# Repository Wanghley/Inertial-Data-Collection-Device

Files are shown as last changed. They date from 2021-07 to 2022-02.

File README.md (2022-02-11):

Inertial Data Collection Device<br>
      

>  printed circuit board and code for collecting inertial data to research purposes of movements.

## About
Hardware developed to collect inertial data from human's hands (i.e. Accelerometer, Giroscope) and temperature in order to provide an open source hardware for research related to the analysis of human movements for many purposes.<br>
This project was tested and focused on the diagnosis and prognosis of neuromotor diseases - mostly Parkinson's Disease as part of the project of scientific research [**"Visualization Strategies to Online Big Data applied in individualized medicine"**](https://github.com/Wanghley/PIBIC-Strategies-Data-Visualization-Medicine).

## Requirements
| Dependency | Platform | Description |
| :--------- | -------- | :---------- |
| [arduino_2012](https://github.com/Wanghley/Inertial-Data-Collection-Device/blob/main/lib/arduino_2012.lbr) | eagle lib | arduino schematic and layout to **Eagle** project |
| [con-headers-jp](https://github.com/Wanghley/Inertial-Data-Collection-Device/blob/main/lib/con-headers-jp.lbr) | eagle lib | schematic and layout of female pin bars to **Eagle** project |
| [DIY modules](https://github.com/Wanghley/Inertial-Data-Collection-Device/blob/main/lib/diy-modules.lbr) | eagle lib | bluetooth adaptor fotoprint and symbol to **Eagle** project |
| [KRE](https://github.com/Wanghley/Inertial-Data-Collection-Device/blob/main/lib/kre.lbr) | eagle lib | borne connector fotoprint and symbol to **Eagle** project |
| [pinhead](https://github.com/Wanghley/Inertial-Data-Collection-Device/blob/main/lib/pinhead.lbr) | eagle lib | added in the **Eagle** project for auxiliary view of pin bars |
| [TimerOne 1.1.0](https://github.com/Wanghley/Inertial-Data-Collection-Device/blob/main/lib/TimerOne-1.1.0.zip) | arduino lib | allow running a periodic interrupt function based in finer PWM control |
| [MPU6050 0.2.1](https://github.com/Wanghley/Inertial-Data-Collection-Device/blob/main/lib/MPU6050-0.2.1.zip) | arduino lib | allow MPU6050 easy control and manipulation |
| [Wire](https://www.arduino.cc/en/reference/wire) | arduino lib | allow communication over I2C protocol |
| [SoftwareSerial](https://www.arduino.cc/en/Reference/softwareSerial) | arduino lib | allow serial communication on other digital pins of the Arduino |

## Bill of Materials
| # | Designator | Qty | Description | Obs |
| - | :--------- | --- | :---------- | :---------- | 
| 1 | R1, R2 | 2 | Resistor 220R 5% (1/4W) | Used for digital protection of bluetooth module RX |
| 2 | HC-05 | 1 | HC-05 Bluetooth Module | Module of Low supply consumption for prototype communication |
| 3 | PUSH | 2 | Push Button Long Head | Push button for hardware control and operation  |
| 4 | ON/OFF | 1 | 255sb sliding switch | Sliding switch to control energy supply of the prototype |
| 5 | LED1 | 1 | COM-09590 | 2.25 V Red LED 5mm Cylindrical indicates the hardware is ready for collection |
| 6 | LED2 | 1 | COM-09590 | 2.25 V green LED 5mm Cylindrical indicates the hardware operation mode and collection in process |
| 6 | Arduino Nano | Arduino Nano | | mother board and controller |
| 7 | KRE-2P | 1 | Borne Connector | Connector to the batery |
| 8 | BATTERY CHARGER | 1 | TP4056 | Power supply adn voltage regulator to the batery |
| 9 | RGB_LED | 1 | LED RBG 5MM | RGB LED 5mm Cylindrical indicates the mode of operation of the device |

## Development
In order to run and contribute to the PCB development you must have **Eagle**  installed in your computer and then use the .sch to work on the circuit itself and the .brd to work in the layout design.

Now, for the development under de code of hardware control you must have Arduino IDE or similar to work on the .ino code plus all the libraries mentioned above on the field [Requirements](#Requirements).

## Versioning
We use [SemVer 2.0.0](https://semver.org/spec/v2.0.0.html) for versioning. For the versions available, see the [tags on this repository](https://github.com/Wanghley/Inertial-Data-Collection-Device/tags).

## Authors
<table>
  <tr>
    <td align="center">
      <a href="https://github.com/wanghley">
        Foto do Wanghley no GitHub<br>
        <sub>
          <b>Wanghley Soares Martins</b>
        </sub>
      </a>
      <p>Researcher</p>
    </td>
    <td align="center">
      <a href="https://github.com/oliveirafhm">
        Foto do prof. Fábio no GitHub<br>
        <sub>
          <b>Fábio Henrique M Oliveira</b>
        </sub>
      </a>
      <p>Research Advisor</p>
    </td>
  </tr>
</table>

See also the list of [contributors](https://github.com/Wanghley/PIBIC-Strategies-Data-Visualization-Medicine/contributors) who participated in this project.

## License
This project is licensed under the CC BY-NC-SA 4.0 License - see the [LICENSE.md](LICENSE.md) file for details

## Acknowledge
*   Remember, the project is free for you to use, manipulate, and change. However, I am just asking you to mention us in any copy, modification as the root of your development. We would also appreciate you citating us in any paper you publish using any knowledge we had developed here.
*   I would advice you to try out the hardware with an analysis of the result data.
*   If you want an easier software for hardware control, check out the [CONTROL SOFTWARE](https://github.com/Wanghley/PIBIC-Strategies-Data-Visualization-Medicine)

## Gallery
General view of the projected PCB. For more images go to [images/](https://github.com/Wanghley/Inertial-Data-Collection-Device/tree/main/images) and if you still want to see more you can see 3D views on [view/](https://github.com/Wanghley/Inertial-Data-Collection-Device/tree/main/view)

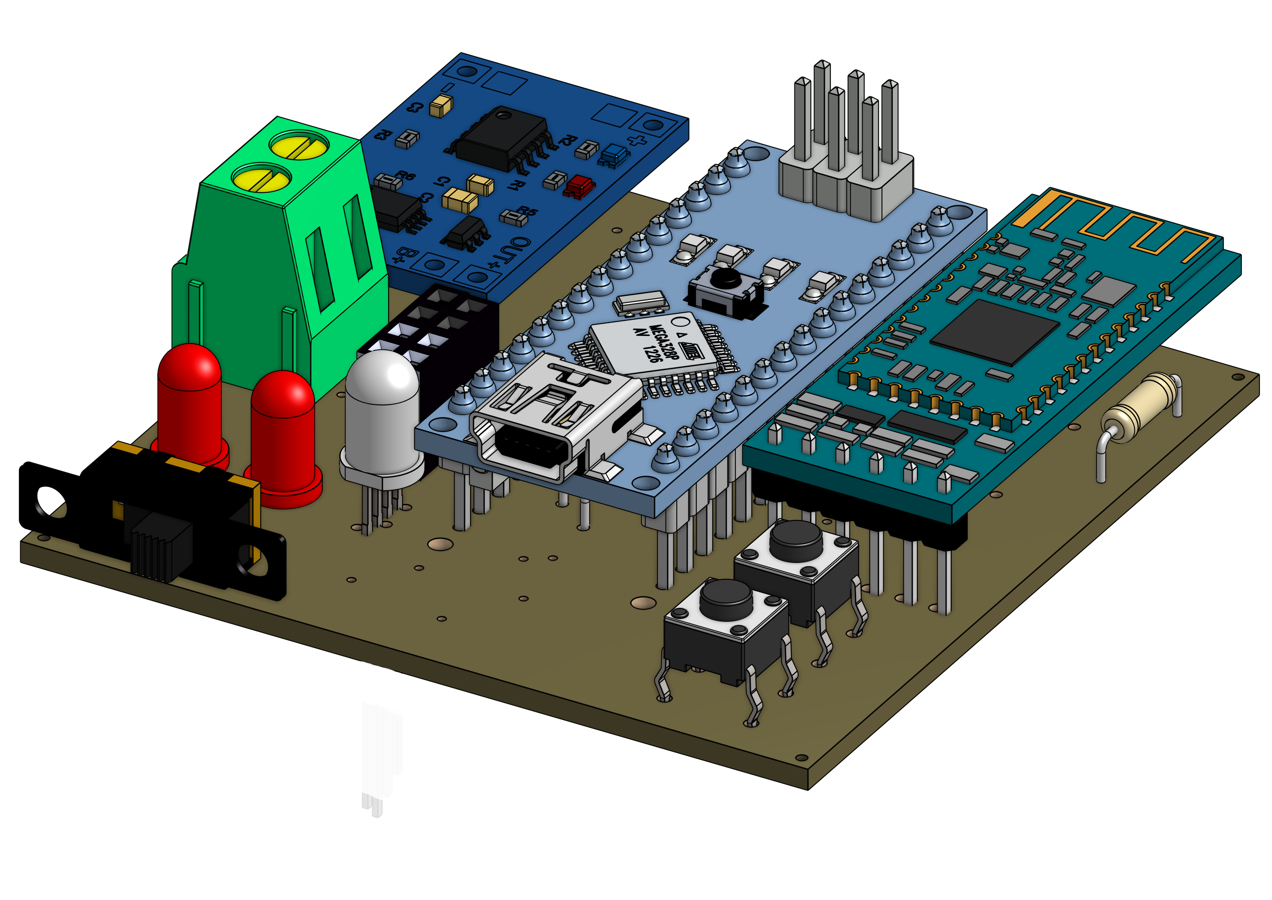
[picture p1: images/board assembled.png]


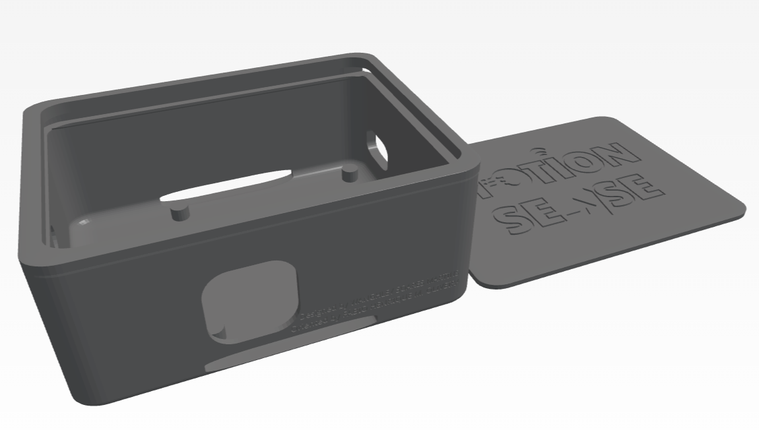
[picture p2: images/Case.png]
Case 3D view


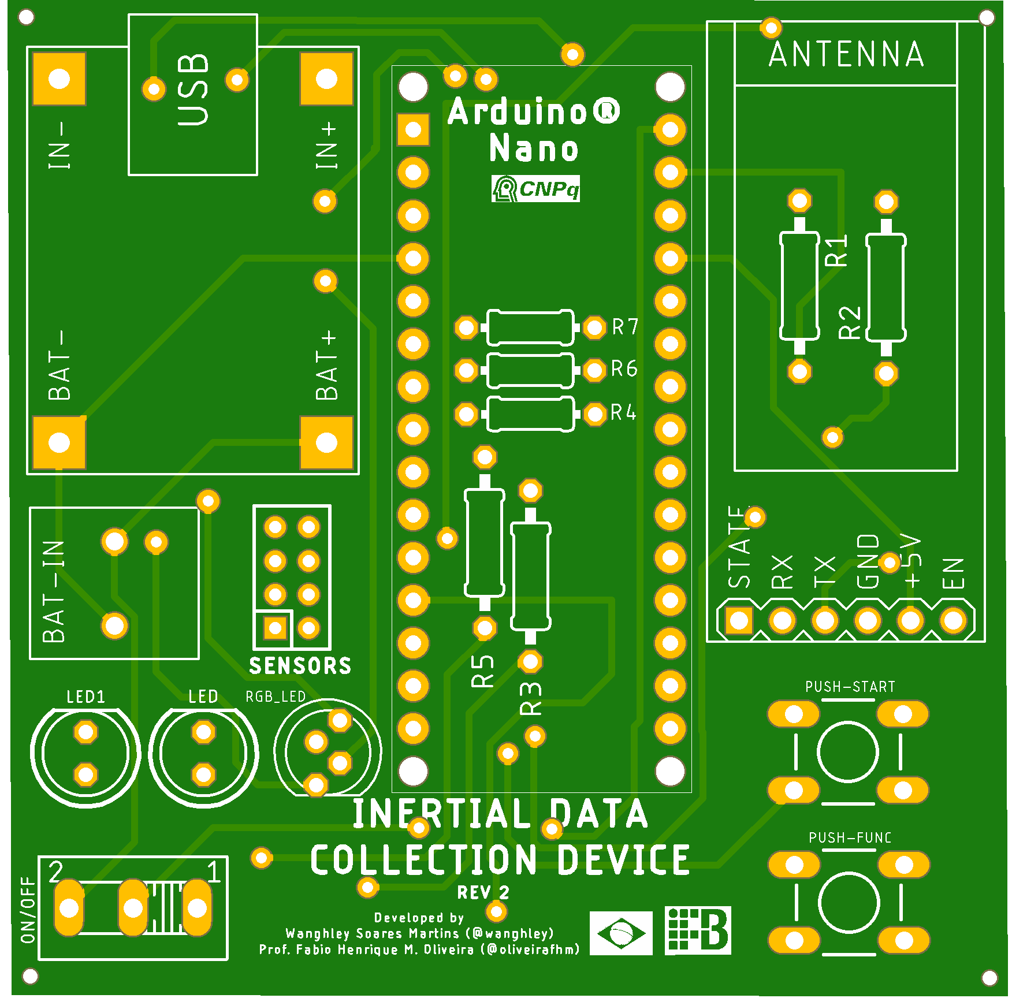
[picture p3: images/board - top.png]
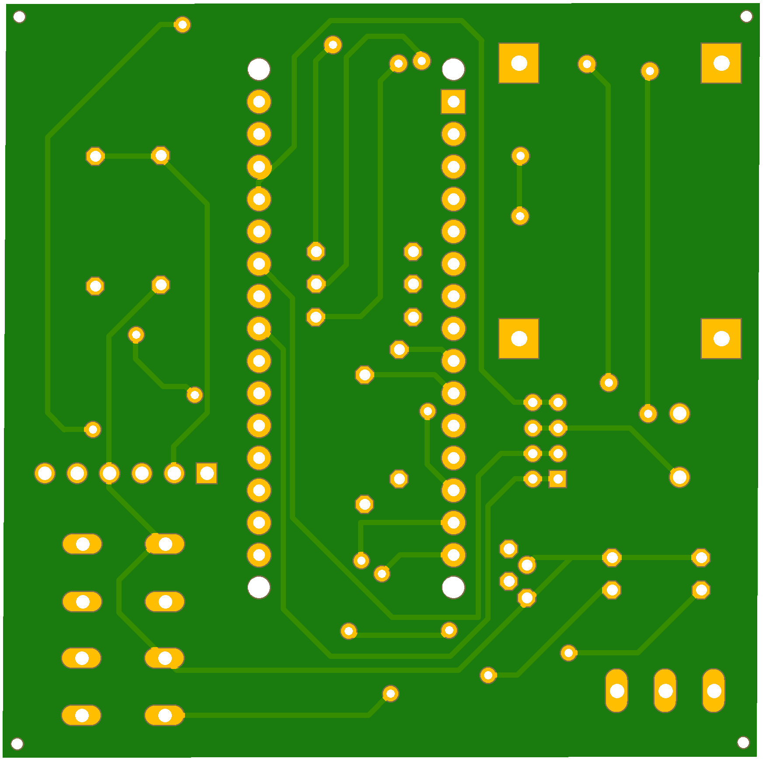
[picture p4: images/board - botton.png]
|  | |
|-|-|

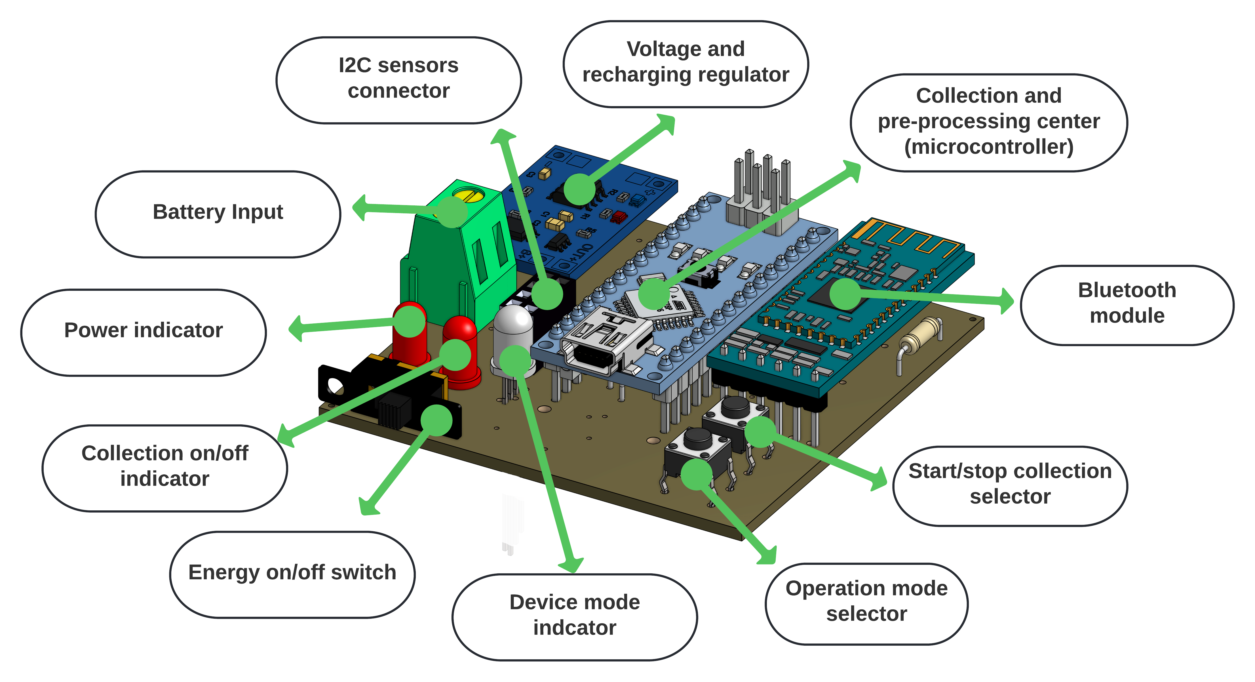
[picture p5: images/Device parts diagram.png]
Device parts diagram


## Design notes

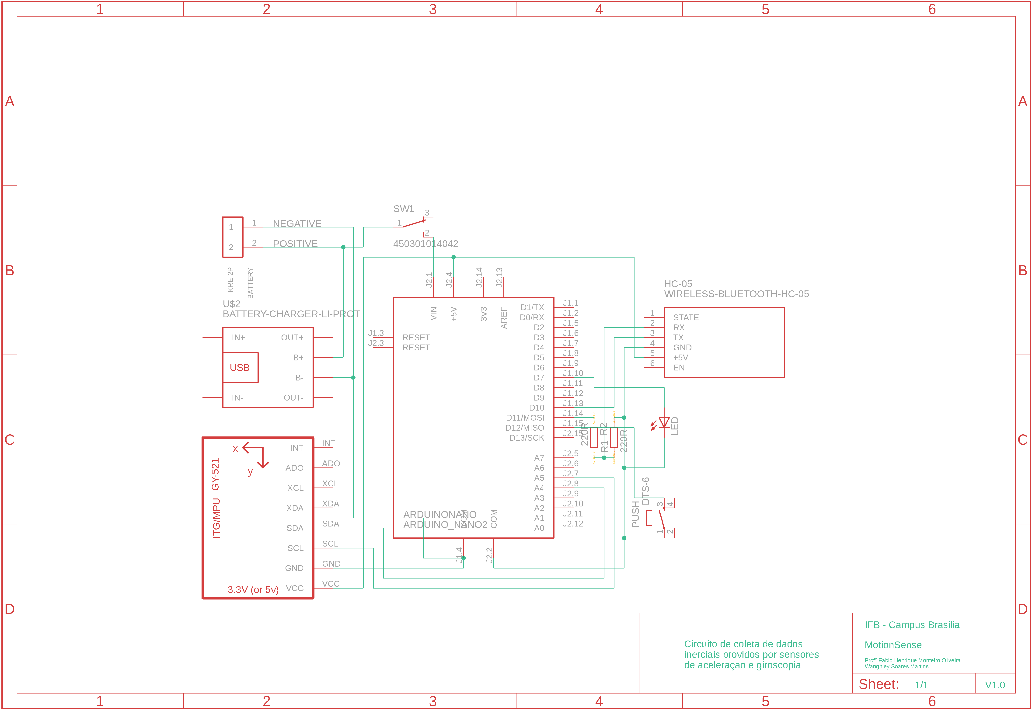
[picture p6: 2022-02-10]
images/sch.png

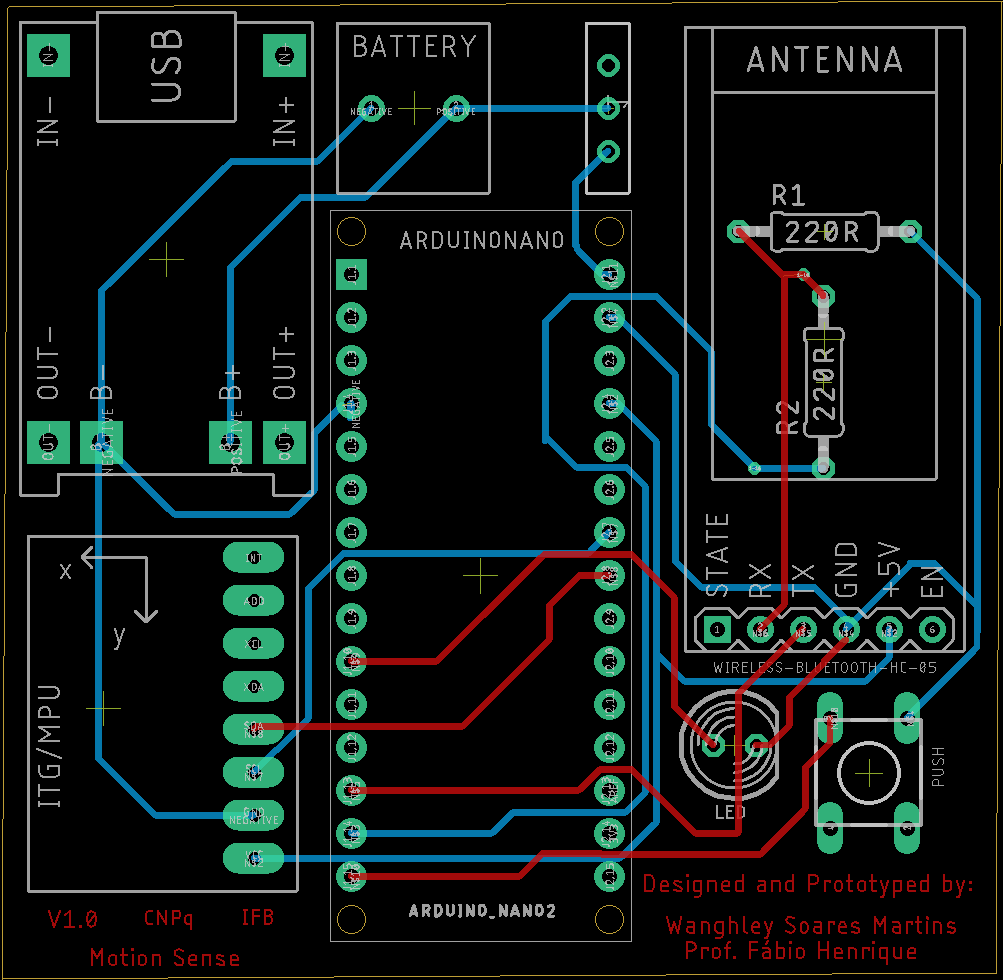
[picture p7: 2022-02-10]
images/pcb.png

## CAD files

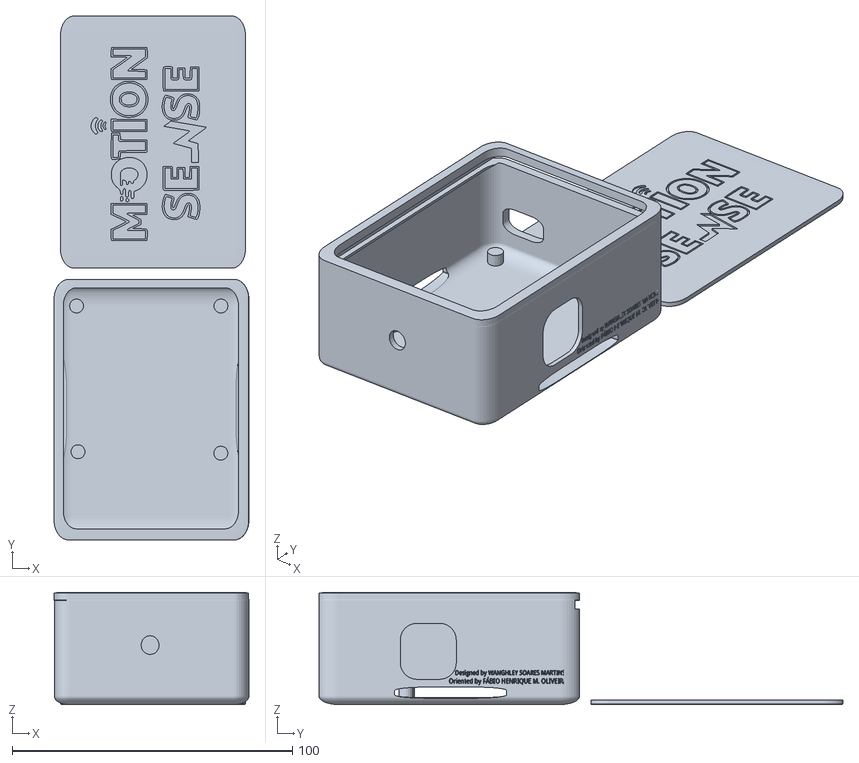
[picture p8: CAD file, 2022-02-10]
component/Complete Motion Sense Box.stl
69.5 x 187.0 x 40.0

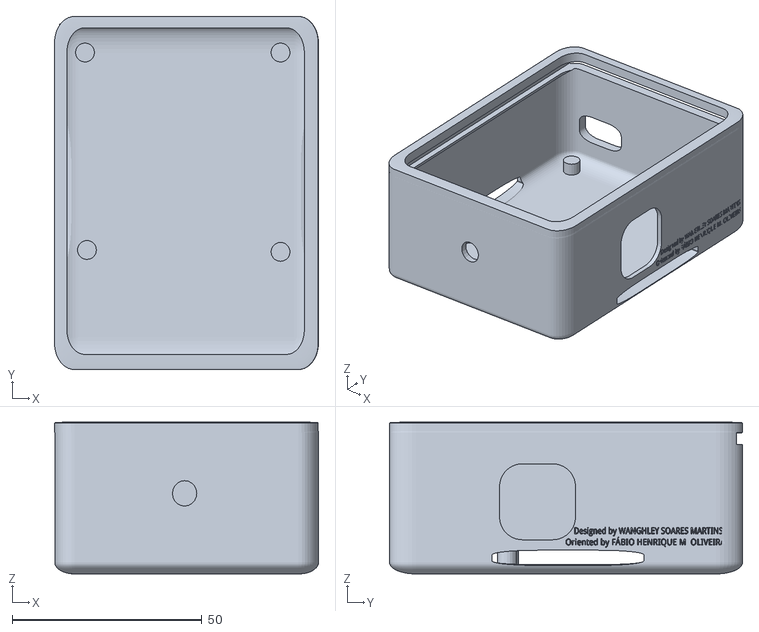
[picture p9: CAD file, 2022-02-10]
component/Case Motion Sense Box.stl
69.5 x 93.0 x 40.0

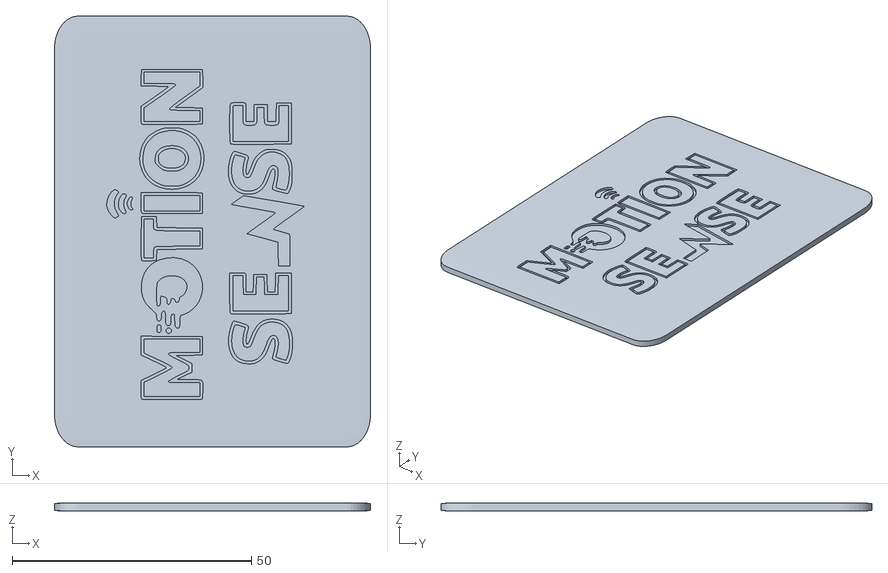
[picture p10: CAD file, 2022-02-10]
component/Cap Motion Sense Box.stl
66.0 x 90.0 x 1.70

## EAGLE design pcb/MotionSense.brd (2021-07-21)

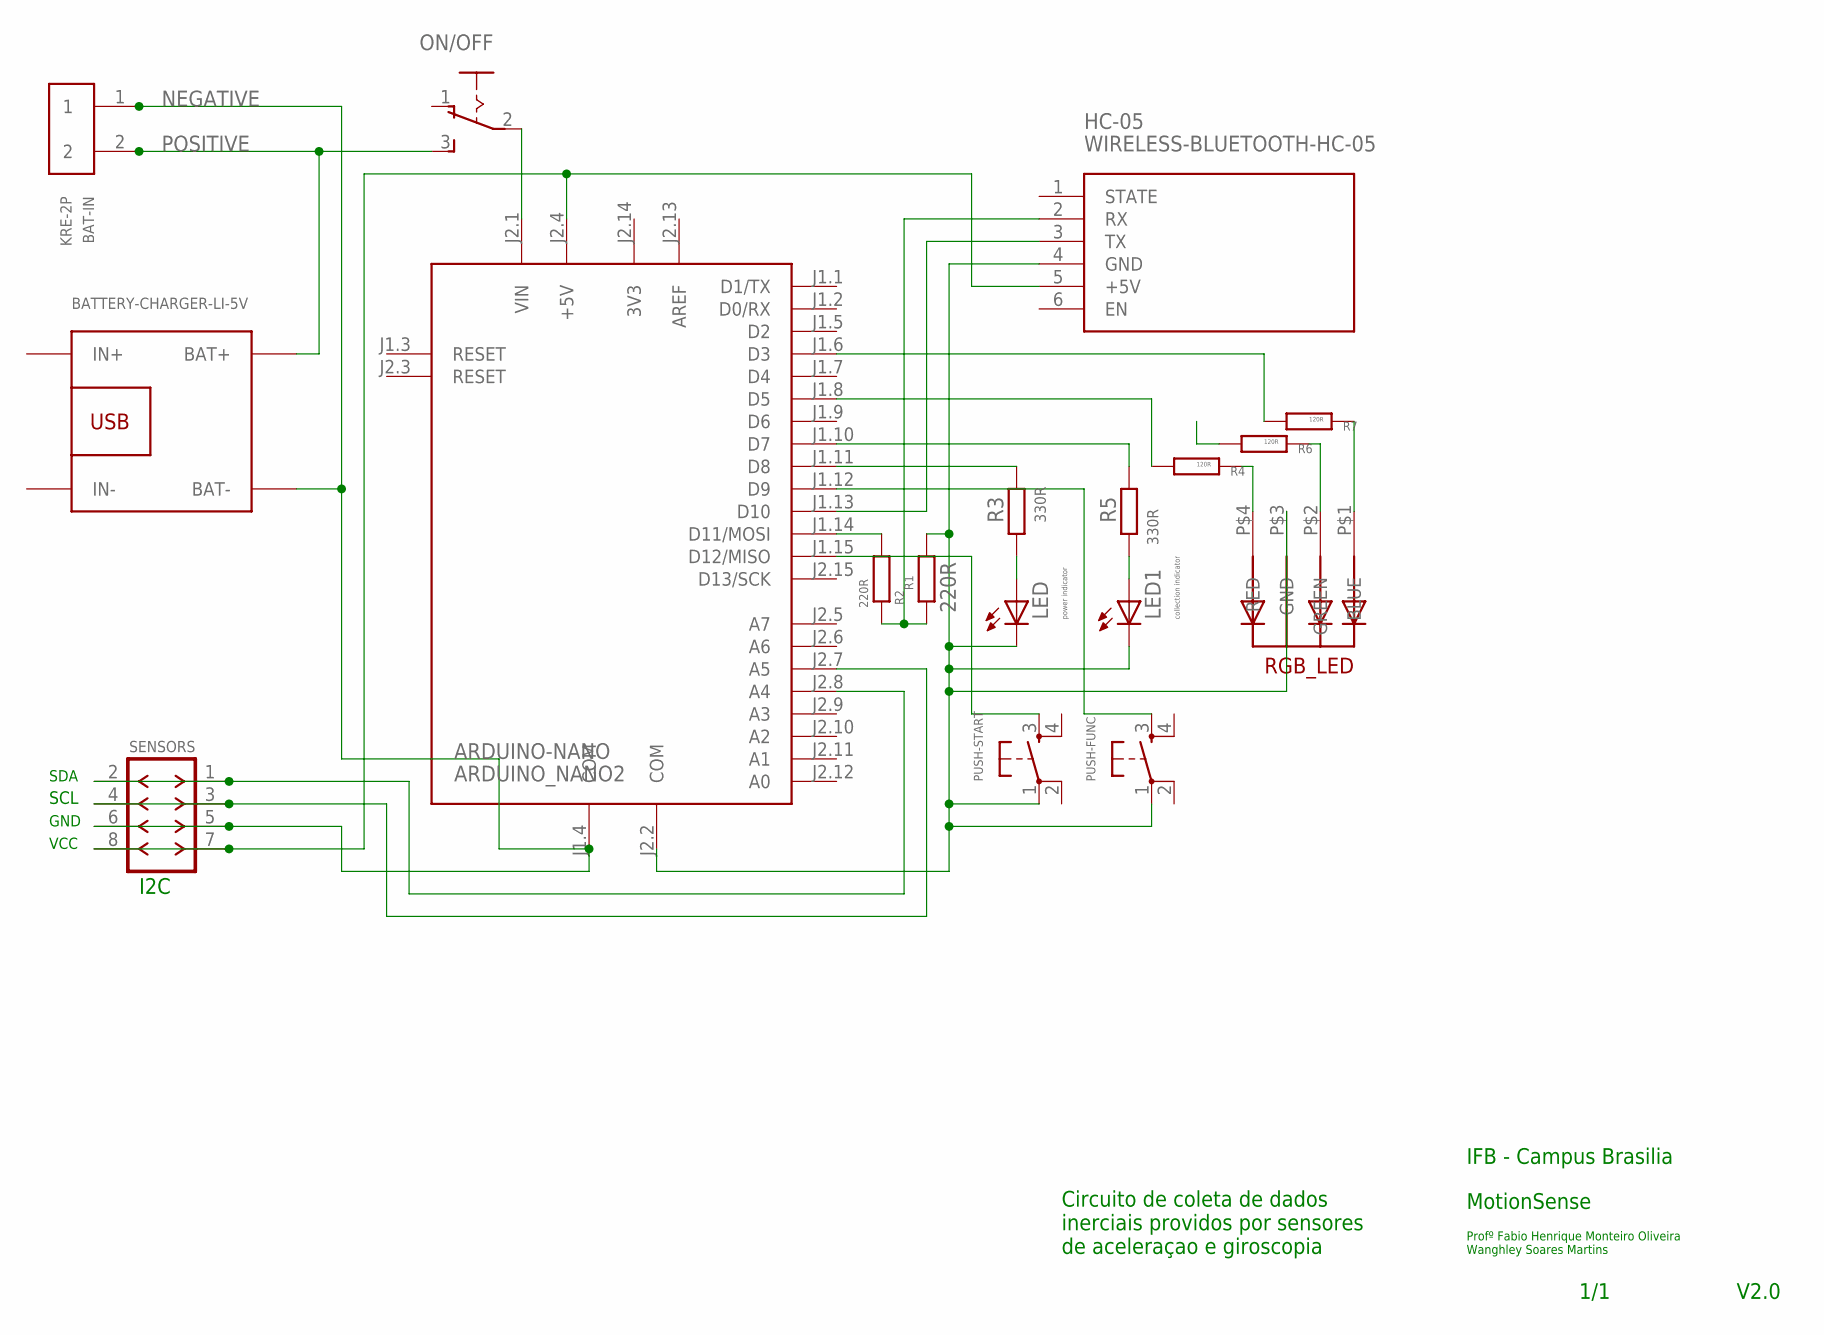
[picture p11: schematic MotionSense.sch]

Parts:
ARDUINO-NANO: ARDUINO_NANO2
BAT-IN: KRE-2P
HC-05: WIRELESS-BLUETOOTH-HC-05
LED: power indicator; LED5MM
LED1: collection indicator; LED5MM
ON/OFF: 255SB
PUSH-FUNC: DTS-6
PUSH-START: DTS-6
R1, R2: 220R; 0207/10
R3, R5: 330R; 0207/10
R4, R6, R7: 120R; 0204/7
RGB_LED: 5MMRGBLED; LED5MMRGB
SENSORS: F-2X04-DIL-2MM_M; DIL-2MM-2X04_M
U$1: BATTERY-CHARGER-LI-5V

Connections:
3V3: ARDUINO-NANO.J2.14 (3V3)
AREF: ARDUINO-NANO.J2.13 (AREF)
unnamed: LED.A, R3.1
unnamed: ARDUINO-NANO.J2.4 (+5V), HC-05.5 (+5V), SENSORS.7, SENSORS.8
unnamed: ARDUINO-NANO.J1.14 (D11/MOSI), R2.1
unnamed: ARDUINO-NANO.J2.2 (COM), HC-05.4 (GND), LED.K (C), LED1.K (C), PUSH-FUNC.1, PUSH-START.1, R1.2, RGB_LED.P$3 (GND)
unnamed: ARDUINO-NANO.J1.13 (D10), HC-05.3 (TX)
unnamed: HC-05.2 (RX), R1.1, R2.2
unnamed: ARDUINO-NANO.J2.7 (A5), SENSORS.3, SENSORS.4
unnamed: ARDUINO-NANO.J2.8 (A4), SENSORS.1, SENSORS.2
unnamed: ARDUINO-NANO.J1.10 (D7), R5.2
unnamed: ARDUINO-NANO.J1.15 (D12/MISO), PUSH-START.3
unnamed: ARDUINO-NANO.J2.1 (VIN), ON/OFF.2
unnamed: ARDUINO-NANO.J1.12 (D9), PUSH-FUNC.3
unnamed: ARDUINO-NANO.J1.11 (D8), R3.2
unnamed: LED1.A, R5.1
unnamed: R4.2, RGB_LED.P$4 (RED)
unnamed: R6.2, RGB_LED.P$2 (GREEN)
unnamed: R7.2, RGB_LED.P$1 (BLUE)
unnamed: ARDUINO-NANO.J1.8 (D5), R4.1
unnamed: ARDUINO-NANO.J1.6 (D3), R7.1
NEGATIVE: ARDUINO-NANO.J1.4 (COM), BAT-IN.1, SENSORS.5, SENSORS.6, U$1.BAT-
POSITIVE: BAT-IN.2, ON/OFF.3 (S), U$1.BAT+

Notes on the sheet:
Circuito de coleta de dados inerciais providos por sensores de aceleraçao e giroscopia
MotionSense
IFB - Campus Brasilia
Profº Fabio Henrique Monteiro Oliveira Wanghley Soares Martins
V2.0
1/1
I2C
VCC
GND
SCL
SDA

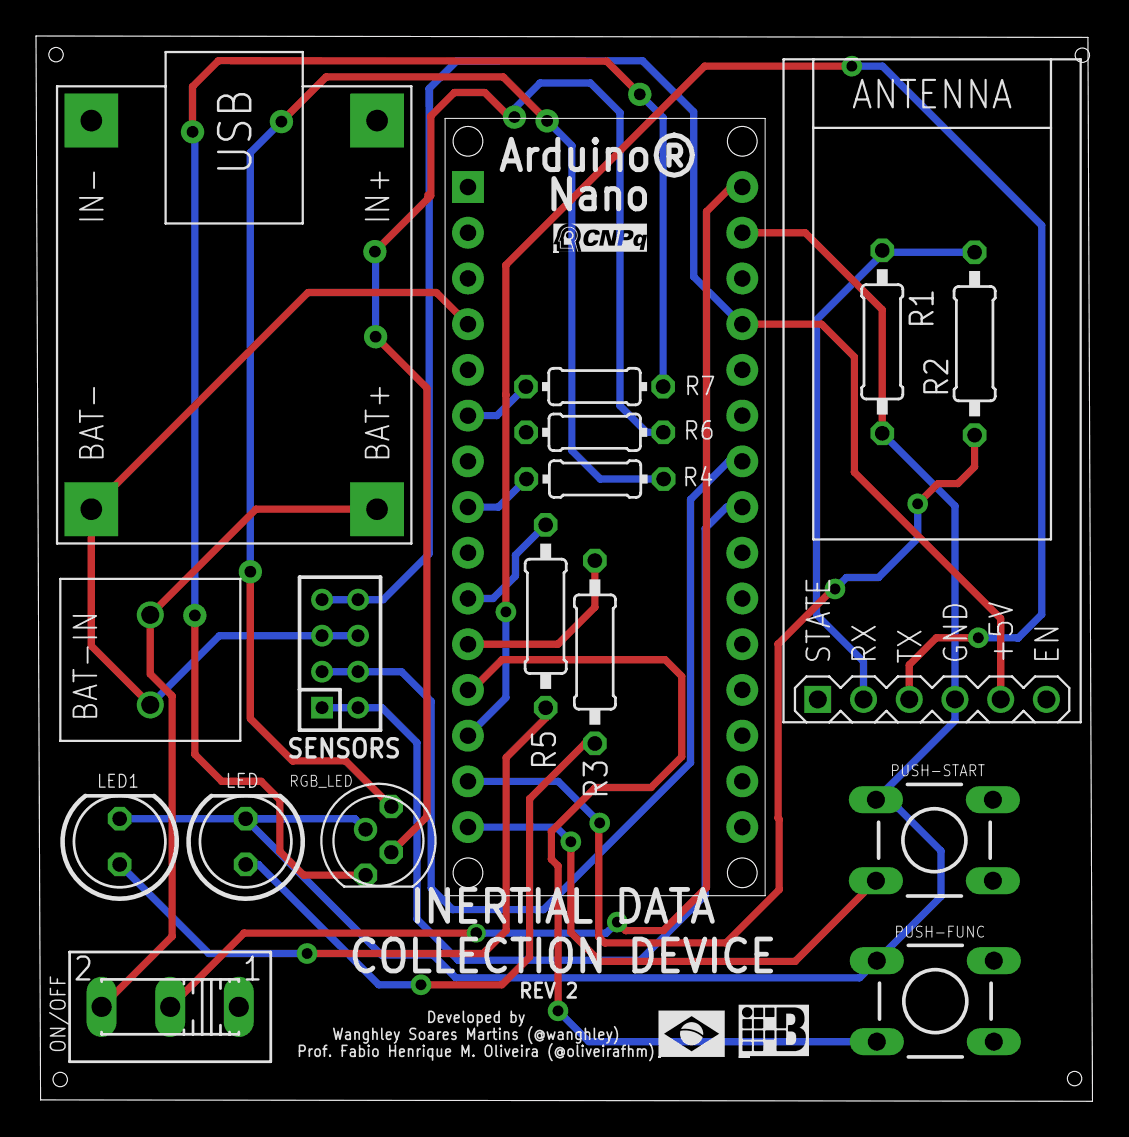
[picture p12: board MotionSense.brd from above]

Board: 2 copper layers, 58.7 x 59.2 mm, 18 parts (0 on the bottom side), 21 nets.

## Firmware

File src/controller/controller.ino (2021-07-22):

/*
AUTHOR: Wanghley Soares Martins (@wanghley)
DATE: April 11, 2019
CONTACT: wanghleys@gmail.com
REV: Fabio Henrique, Lissa Ximenes
DATE: Sep 19, 2019
*/
#include <TimerOne.h>       // Library for timer interrupt
#include <MPU6050.h>        // Standard library for manipulation on the MPU6050
#include <Wire.h>           // Control library of the I²C protocol, used by the MPU6050
#include <SoftwareSerial.h> // Bluetooth control library

#define BTNMODE 9 //Button for mode selection
#define BTNCOLLECTION 12 //Button for start collection
#define POWERLED 8 //LED power indicator
#define COLLECTLED 7 //LED collection happening indicator

// LED for indication of operation mode: Standalone, Serial, MotionSense
#define OPERATIONLED_RED 5 //Standalone
#define OPERATIONLED_BLUE 3 //Serial
#define OPERATIONLED_GREEN 6 //MotionSense

SoftwareSerial BTSerial(10, 11); // RX | TX

const int MPU = 0x68; // MPU6050 address on the I²C bus (available in datasheet)
volatile bool allowSensorReading = false; // responsible for allowing the data reading from teh I2C sensor
bool handshaked = false; // Variable of flow control - handshake
bool collectionStarted = false; // Variable of control of collection procedure
double AcX, AcY, AcZ, Tmp, GyX, GyY, GyZ; // Variables used to store data
char a, c='1';
volatile bool flag = false;
bool authSendData;
long Micros;
const int STANDALONE[3] = {255,0,0}; //1
const int SERIALDATA[3] = {0,0,255}; //2
const int MOTIONSENSE[3] = {0,255,0}; //0
int operation = 0;
int val = -1;

void setup()
{
    /*Bluetooth comunication: 
      Module - HC-05
      Password - 1234
    */
    Wire.begin();                // I²C communication starts
    Wire.beginTransmission(MPU); // Indicates the address of the MPU to start communication
    Wire.write(0x6B);            // Indicates the MPU that the communication will start
    Wire.write(0);               // Indicates the MPU that wants to leave the communication on standby
    Wire.endTransmission(true);  // Disables communication

    Serial.begin(57600);
    Serial.println("==================================================");
    Serial.println("|                   MOTIONSENSE                  |");
    Serial.println("|       Open Parkinson's Diagnostic Device       |");
    Serial.println("==================================================");
    BTSerial.begin(57600); // HC-05 default speed in AT command more

    // starts the sample rate by time (clock)
    Timer1.initialize(20000); // Adjusted for 50hz = 10⁶ / 50 = 20,000ms
    Timer1.attachInterrupt(changeFlag); // Indicates the function that will be called every 20,000ms

    //start LEDS default
    pinMode(BTNCOLLECTION,INPUT_PULLUP);
    pinMode(BTNMODE,INPUT_PULLUP);
    pinMode(COLLECTLED,OUTPUT);
    digitalWrite(COLLECTLED,LOW);
    pinMode(POWERLED,OUTPUT);
    digitalWrite(POWERLED,HIGH);

    //RGB
    pinMode(OPERATIONLED_RED,OUTPUT);
    pinMode(OPERATIONLED_BLUE,OUTPUT);
    pinMode(OPERATIONLED_GREEN,OUTPUT);

    RGB_color(MOTIONSENSE);
}

void stopProcedure(){
  noInterrupts();
  allowSensorReading = false;
  collectionStarted = false;
  flag = false;
  handshaked = false;
  digitalWrite(COLLECTLED,LOW);
  interrupts();
  
}

//Function that controls the RGB mode indicator LED
void RGB_color(int color[])
 {
  analogWrite(OPERATIONLED_RED, color[0]);
  analogWrite(OPERATIONLED_GREEN, color[1]);
  analogWrite(OPERATIONLED_BLUE, color[2]);
}

//Function that get the micros of the devide and indicates the flag authorization to send data
void changeFlag(){
  if (allowSensorReading){
    flag = true; // active data display
    Micros = micros();
  }    
}

void loop(){
  //COLLECTION BUTTON ON/OFF CONTROLL
  if(digitalRead(BTNCOLLECTION)==LOW){
   if(collectionStarted==true){ //Close the collection procedure by hardware interaction BTN
     Serial.print("stopping... ");
     // TODO write the function to clean buffer and send everything that was collected
     collectionStarted = false;
     BTSerial.write("stop#");
     digitalWrite(COLLECTLED,LOW);
     Serial.println("STOPPED");
   }else{
     Serial.print("starting... ");
     // TODO write the function to clean buffer and start collection from beginning
     collectionStarted=true;
     digitalWrite(COLLECTLED,HIGH);
     Serial.println("STARTED");
     switch(operation){
      case 1:
        Serial.println("> STANDALONE mode");
        break;
      case 2:
        Serial.println("> SERIALDATA mode");
        break;
      default:
        Serial.println("> MOTIONSENSE mode");
        break;
     }
   }
   delay(350); //manual delay adjustment when button is pressed
  }
  if(digitalRead(BTNMODE)==LOW){
    if(!collectionStarted){
      if(operation==0){
        operation+=1;
        RGB_color(STANDALONE);
      } else if(operation==1){
        operation+=1;
        RGB_color(SERIALDATA);
      } else {
        operation=0;
        RGB_color(MOTIONSENSE);
      }
    }
    delay(350);
  }
  //==========================================================================
  
  //SOFTWARE CLOSURES COMMANDS - BLE & SERIAL
  if (collectionStarted){ 
    if(operation==0){
      if(BTSerial.available()){ //Close connection by software attempt - through BLE command f
       a = (char)BTSerial.read(); //Wait for the
       if(a=='f'){
        BTSerial.flush();//Descarrega o buffer
        BTSerial.write("stop#");
        stopProcedure();
        Serial.println("FINISHED!\nReady for next...");
       }
    }
    if (Serial.available()){//Close connection by software attempt - through Serial console by cable
      a = Serial.read();
      if (a == 'f'){
        BTSerial.write("stop#");
        BTSerial.flush(); //Descarrega o buffer
        stopProcedure();
        Serial.println("FINISHED!\nReady for next...");
        Serial.println("==================================================");
      }
    }  
  }
  //==========================================================================

    noInterrupts();// From here interruptions are not allowed
    authSendData = flag; // authorization for send data - change at each time interruption time - default 50Hz
    flag = false; // set the flag back to original state
    interrupts(); // From here interruptions are allowed
    
    if (authSendData){ // control of data sending - based on the time interruption
      switch(operation){
      case 1:
        sendDataBluetooth();
        break;
      case 2:
        sendDataSerial();
        break;
      default:
        sendDataBluetooth();
        break;
     }
    }
    //==========================================================================

    //THREE WAY HANDSHAKE
    if(!handshaked){
      if(operation==0){
        val = BTSerial.read(); // Read data comming from the bluetooth
        c='1'; // Variable 
        if (val != -1){
            c = val;
        }
        if (c == 's'){ //First 3-way call - command received
          Serial.println("> Handshake started!\n>> Waiting final handshake");
          BTSerial.write("ok#"); //2nd 3-way call - acknowledge sent
          BTSerial.flush(); //clean buffer
          while (!handshaked){
            val = BTSerial.read();
            if (val != -1){
              c = val;
              if(c=='c'){
                handshaked = true;
                Serial.println("HANDSHAKE SUCCESSED!");
                Serial.println("==================================================");
                allowSensorReading = true;
              }
            }
          }
        }
      }else{
        handshaked=true;
        allowSensorReading = true;
        Serial.println("STARTED!");
        Serial.println("==================================================");
      }  
    }
    //==========================================================================

    //GETTING DATA FROM SENSOR
    if (allowSensorReading){
        Wire.beginTransmission(MPU); //Indicates the resumption of i²c communication
        Wire.write(0x3B);            /*initiate the register of the MPU6050, indicating that it will receive data*/
        Wire.endTransmission(false); //initiate stable communication again
        //Request sensor data
        Wire.requestFrom(MPU, 14, true);
        getData(); // Keep reading from HC-05
    }
    //==========================================================================
  }
}

//Função que recebe os dados do MPU6050 e
//faz as conversões do valor bruto para acc = g e gy = º/seg
void getData(){
  //Armazena o valor dos sensores nas variaveis correspondentes
  AcX = Wire.read() << 8 | Wire.read(); //0x3B (ACCEL_XOUT_H) & 0x3C (ACCEL_XOUT_L)
  AcY = Wire.read() << 8 | Wire.read(); //0x3D (ACCEL_YOUT_H) & 0x3E (ACCEL_YOUT_L)
  AcZ = Wire.read() << 8 | Wire.read(); //0x3F (ACCEL_ZOUT_H) & 0x40 (ACCEL_ZOUT_L)
  Tmp = Wire.read() << 8 | Wire.read(); //0x41 (TEMP_OUT_H) & 0x42 (TEMP_OUT_L)
  GyX = Wire.read() << 8 | Wire.read(); //0x43 (GYRO_XOUT_H) & 0x44 (GYRO_XOUT_L)
  GyY = Wire.read() << 8 | Wire.read(); //0x45 (GYRO_YOUT_H) & 0x46 (GYRO_YOUT_L)
  GyZ = Wire.read() << 8 | Wire.read(); //0x47 (GYRO_ZOUT_H) & 0x48 (GYRO_ZOUT_L)
  
  
  //Dados recebidos em 2g
  AcX = AcX / 16384.0;        //Conversão para G
  AcY = AcY / 16384.0;        //Conversão para G
  AcZ = AcZ / 16384.0;        //Conversão para G
  Tmp = Tmp / 340.00 + 36.53; //Conversão para ºC
  GyX = GyX / 250.0;          //Conversão para º/seg
  GyY = GyY / 250.0;          //Conversão para º/seg
  GyZ = GyZ / 250.0;          //Conversão para º/seg
}

void sendDataBluetooth(){
  BTSerial.print((String)Micros+","+(String)AcX+","+(String)AcY+","+(String)AcZ+","+(String)GyX+","+(String)GyY+","+(String)GyZ+","+(String)Tmp+"#");
  BTSerial.flush();
//  Serial.println((String)Micros+","+(String)AcX+","+(String)AcY+","+(String)AcZ+","+(String)GyX+","+(String)GyY+","+(String)GyZ+","+(String)Tmp+"#");
}
void sendDataSerial(){
  Serial.println((String)Micros+","+(String)AcX+","+(String)AcY+","+(String)AcZ+","+(String)GyX+","+(String)GyY+","+(String)GyZ+","+(String)Tmp+"#");
  Serial.flush();
//  Serial.println((String)Micros+","+(String)AcX+","+(String)AcY+","+(String)AcZ+","+(String)GyX+","+(String)GyY+","+(String)GyZ+","+(String)Tmp+"#");
}

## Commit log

2021-07-21 [UPDATE] Wrong ports and errors in design fixing
    [MotionSense.brd]
2021-07-21 [UPDATE] Fixing airwire, dimesion, drill distance & overlap errors in electronic design
    [MotionSense.brd]
2021-07-21 [UPDATE] power and collection led connection inverted correction
    [MotionSense.sch]
2021-07-21 [UPDATE] connecting new wires to LEDs after schematic error correction
    [MotionSense.brd]
2021-07-21 [UPDATE] firmware led inverted correction for compatibility between previous hardware and newer versions
2022-02-10 [UPDATE] device parts diagram in EN added
2022-02-10 [UPDATE] Box (case) view added
2022-02-10 [REFACTOR] using right versioning technique for assembled picture view of the prototype
2022-02-10 [REFACTOR] using right versioning technique for board view
2022-02-10 [REFACTOR] using right versioning technique for pcb and sch view
2022-02-10 [ADD] Box case 3D modeling added
    [Complete Motion Sense Box.stl]
2022-02-10 [ADD] Cap case 3D modeling added
    [Cap Motion Sense Box.stl]
2022-02-10 [ADD] Case 3D modeling added
    [Case Motion Sense Box.stl]

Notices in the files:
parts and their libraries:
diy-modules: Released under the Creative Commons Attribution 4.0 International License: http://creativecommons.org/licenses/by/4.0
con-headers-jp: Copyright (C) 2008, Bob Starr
